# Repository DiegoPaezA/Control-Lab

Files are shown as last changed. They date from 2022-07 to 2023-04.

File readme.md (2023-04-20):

# Low-cost control laboratory kit - Control(LAB)

<p align="justify">Control(Lab) is developed following the <a href="https://is.gd/1HAwDJ">TCLab</a> idea: a printed circuit board (PCB) that allows connection with the Arduino processing unit. The board has three transistors that work as heaters and three temperature sensors to follow the temperature variations in each heater. The operation of the plant is based on the control of the electrical current that flows through the transistors using the pulse width modulation (PWM) generated from the system's processing unit. The control action generates a variation in the temperature of the plant heaters limited by software to 100°C. This variation is measured by the temperature sensors and registered in the Arduino, thus establishing a closed control loop.</p>

<p align="justify">To develop an affordable and easy-to-build control lab kit, low-cost and easily accessible elements were selected. The LM35 temperature sensor replaced the TMP36 temperature sensor used in the TCLAB reference plant; the new sensor fulfills the necessary operating and functionality ranges. The sensor is linear and generates a voltage output proportional to the temperature variation (T° C = 10mV). Also, it has calibrated precision of 1°C, its measurement range is -55 ° C to 150 ° C, and it has a guaranteed precision of 0.5°C at 25°C ambient temperature. Finally, the configuration of three TIP31C NPN transistors (BJTs) as heaters allows implementing controllers of the single-input-single-output (SISO) type or multiple-input multiple-output (MIMO) with a low-cost and accessible device. Figure 1 shows the Control kit (Lab).</p>

<p align="justify">This repository presents different examples focused on testing the operation of the different ESP32 functionalities using FreeRTOS. The examples have been validated using an ESP32 DEVKIT DOIT board and the documentation of each of the examples is being done to address the theoretical concepts of each of the topics addressed.</p>

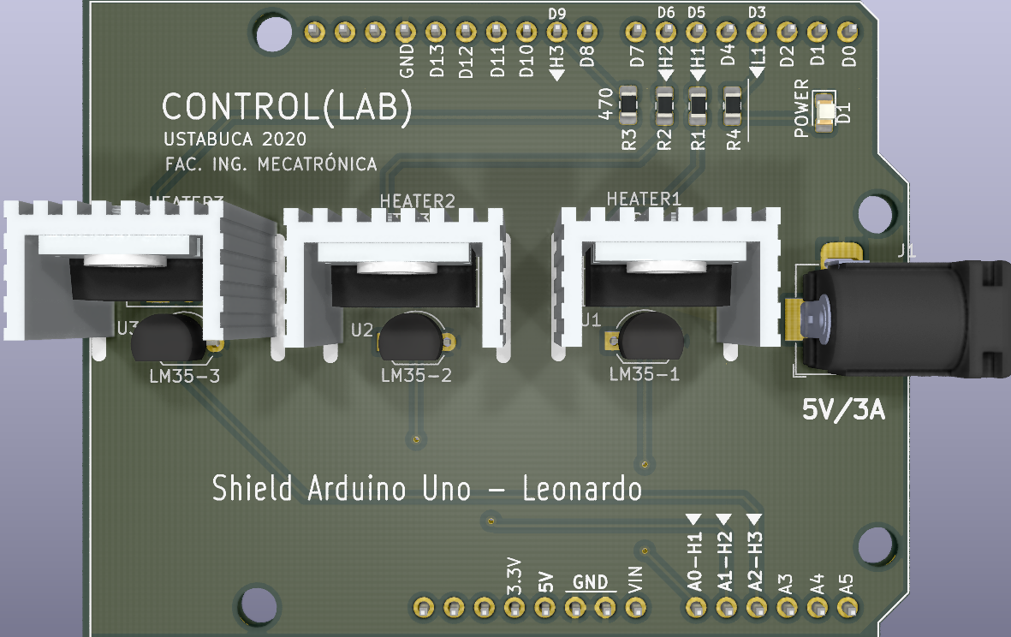
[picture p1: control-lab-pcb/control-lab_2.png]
Control Laboratory Kit - Control(Lab)


## References

Detailed description of the Control(Lab) can be find on the on the Article: [Comparative Study of PID, DMC, and Fuzzy PD+I Controllers in a Control Laboratory Kit](https://ieeexplore.ieee.org/document/9981589)

D. P. Ardila, D. M. Reyes, C. V. Niño, R. Tanscheit and M. Vellasco, "Comparative Study of PID, DMC, and Fuzzy PD+I Controllers in a Control Laboratory Kit," 2022 IEEE Latin American Conference on Computational Intelligence (LA-CCI), Montevideo, Uruguay, 2022, pp. 1-6, doi: 10.1109/LA-CCI54402.2022.9981589.

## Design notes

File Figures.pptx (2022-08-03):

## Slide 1

Fuzzy PD+I

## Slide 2

DMC

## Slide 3

PID

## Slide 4

Fuzzy PD+I + GA

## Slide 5

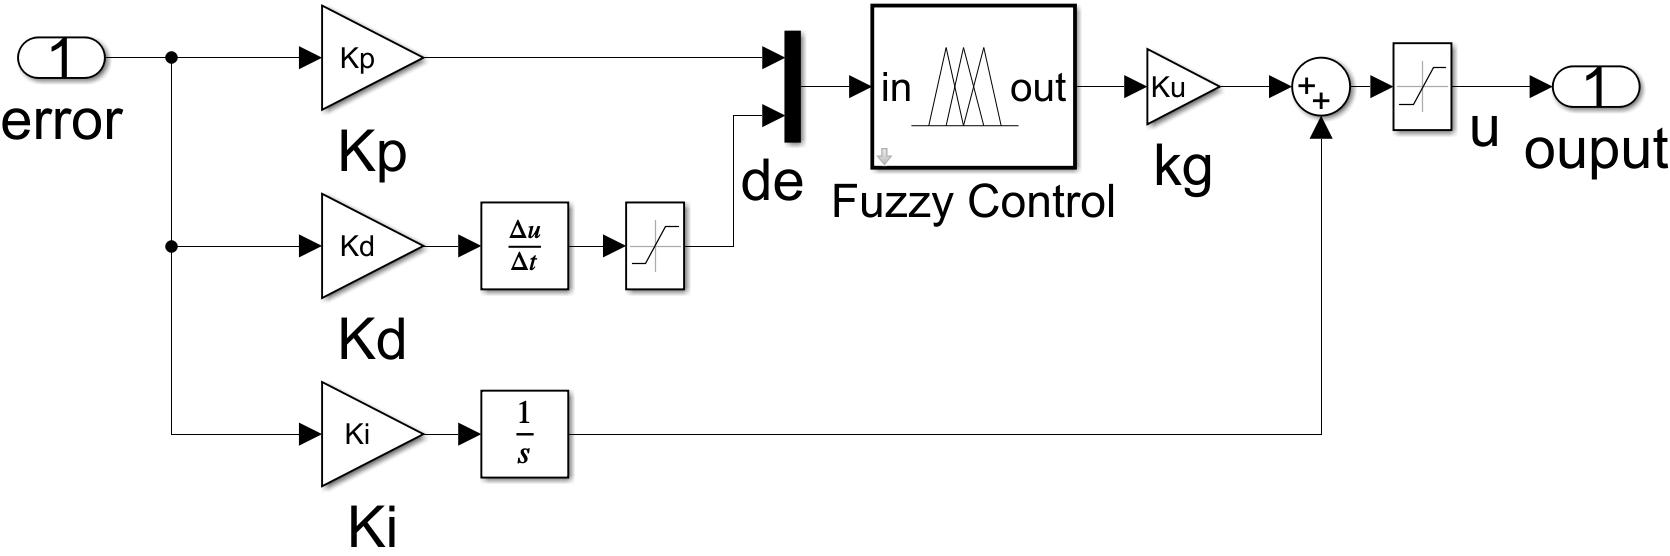
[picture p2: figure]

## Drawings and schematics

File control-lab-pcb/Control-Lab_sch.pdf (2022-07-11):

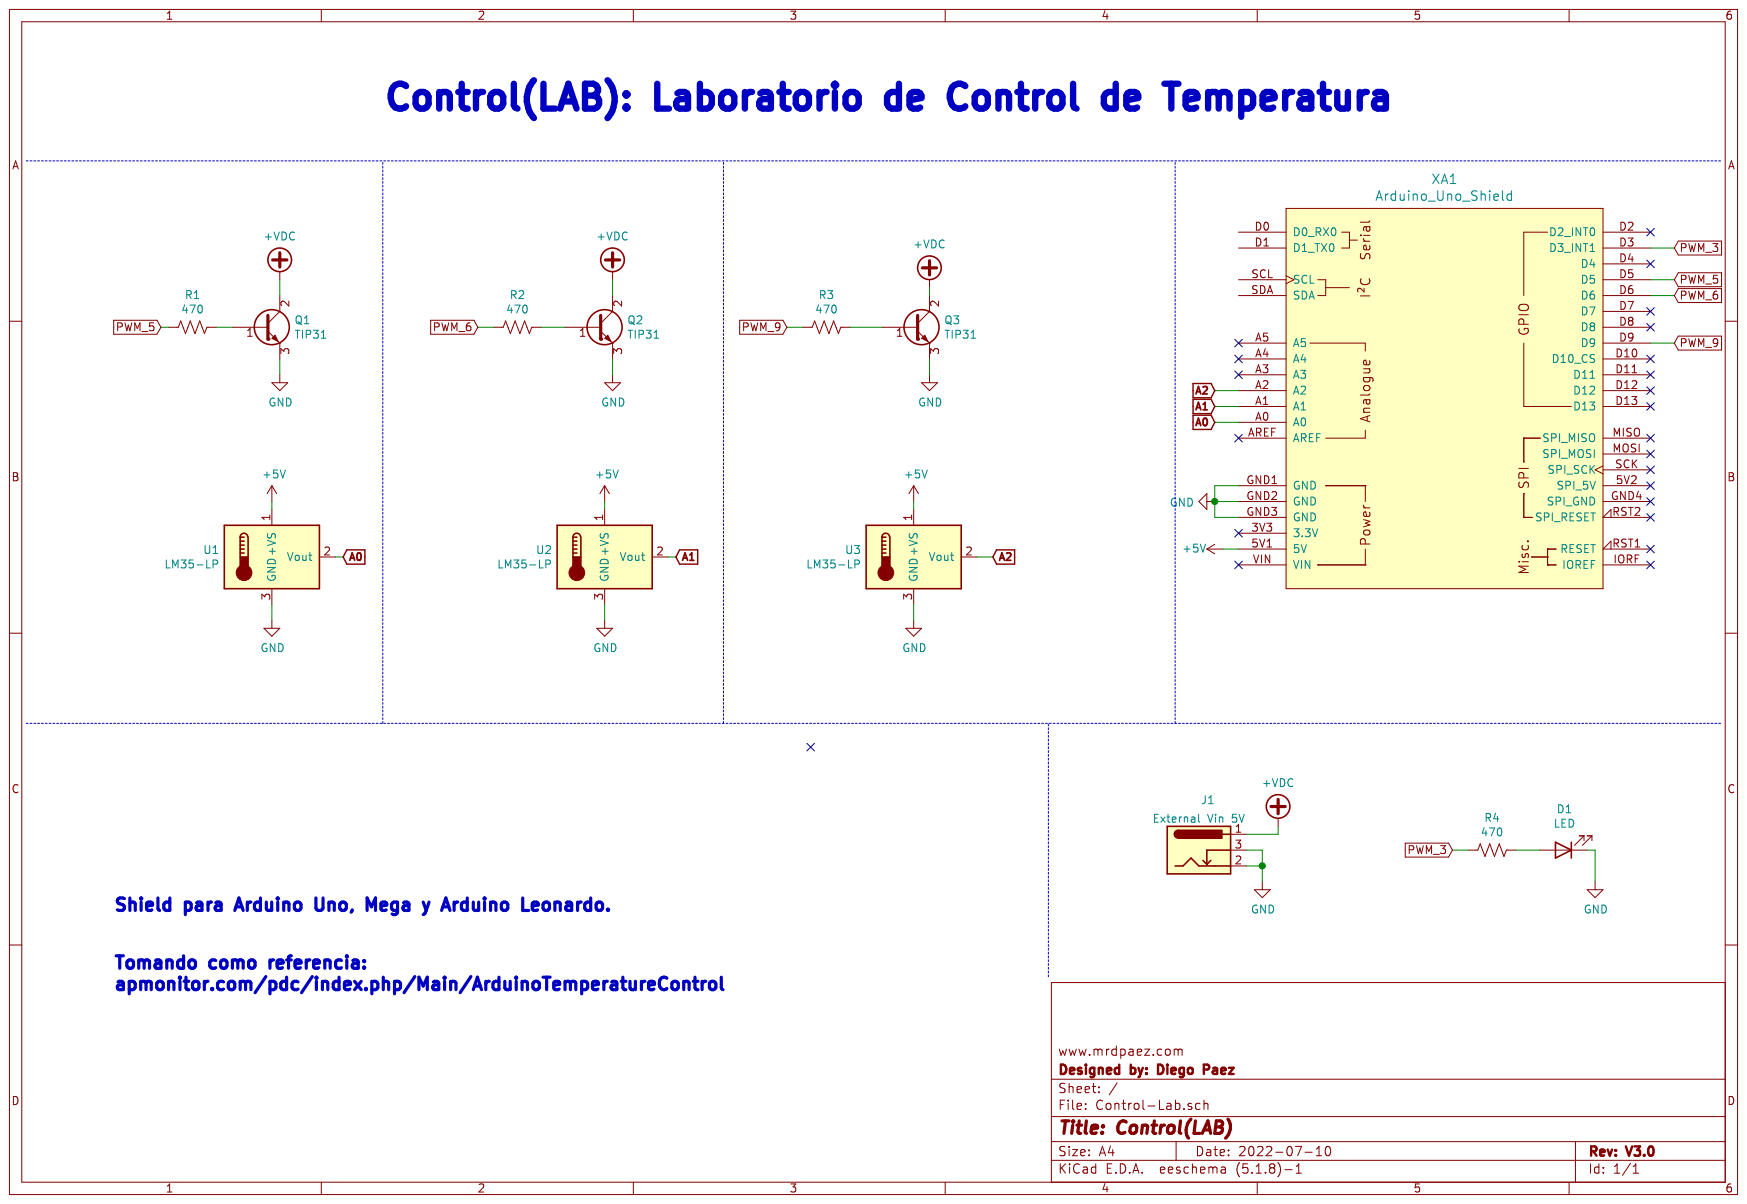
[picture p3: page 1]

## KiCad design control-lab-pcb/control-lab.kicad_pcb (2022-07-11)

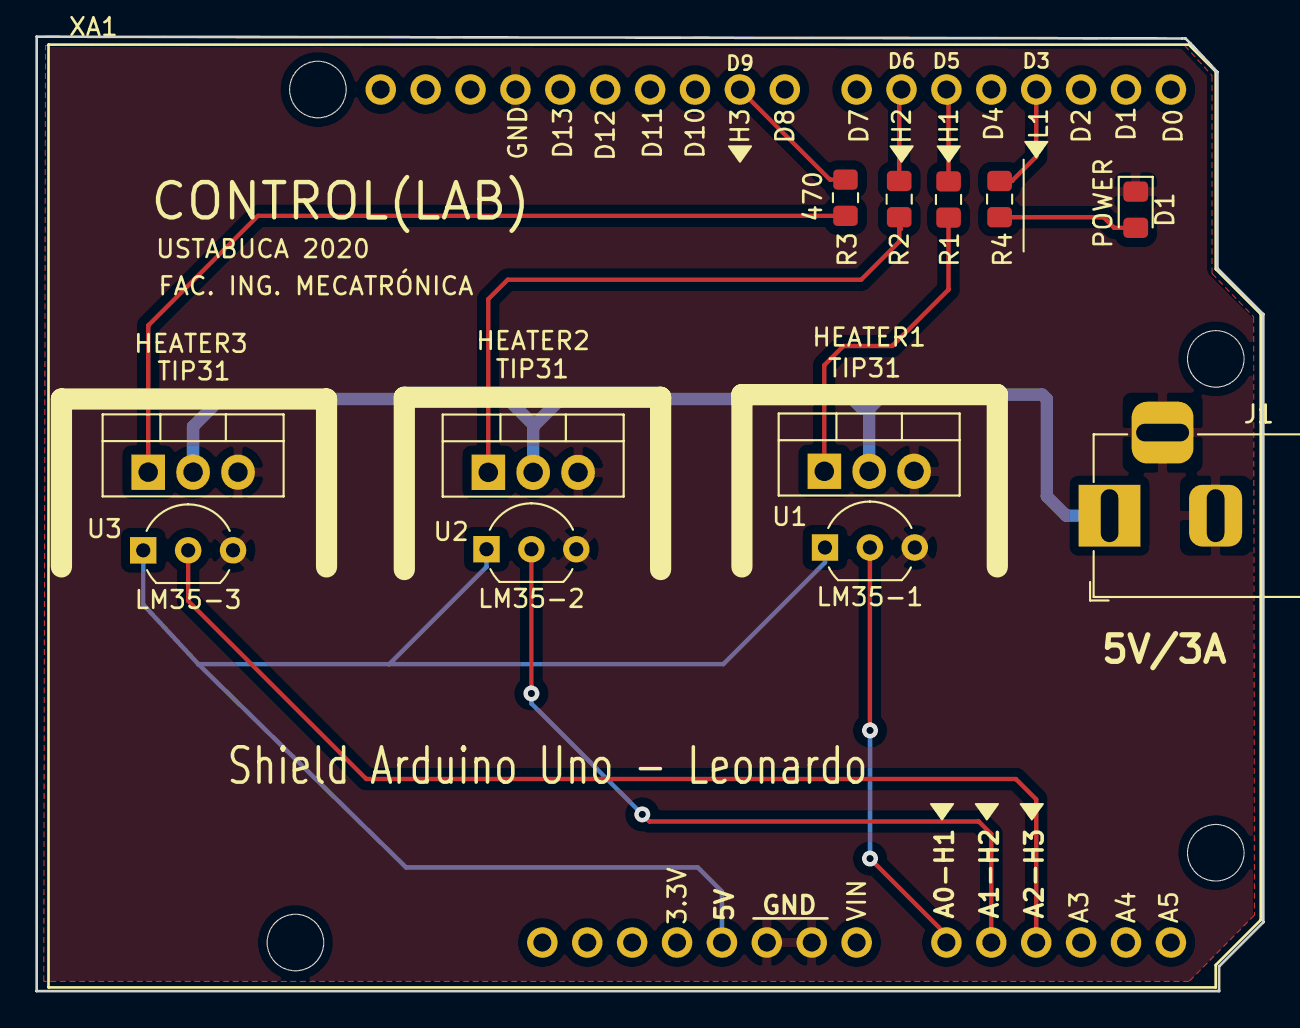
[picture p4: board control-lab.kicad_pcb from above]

Board: 2 copper layers, 69.4 x 54.0 mm, 13 parts (0 on the bottom side), 14 nets.

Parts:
D1: POWER; LED_0805_2012Metric_Pad1.15x1.40mm_HandSolder
HEATER1, HEATER2, HEATER3: TIP31; TO-220-3_Vertical
J1: External Vin 5V; BarrelJack_Horizontal
R1, R2, R3, R4: 470; R_0805_2012Metric_Pad1.15x1.40mm_HandSolder
U1: LM35-1; TO-92_Inline_Wide
U2: LM35-2; TO-92_Inline_Wide
U3: LM35-3; TO-92_Inline_Wide
XA1: Arduino_Uno_Shield; Arduino_Leonardo_Shield

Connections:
+5V: U1.1, U2.1, U3.1, XA1.5V1
+VDC: HEATER1.2, HEATER2.2, HEATER3.2, J1.1
A0: U1.2, XA1.A0
A1: U2.2, XA1.A1
A2: U3.2, XA1.A2
GND: D1.1, HEATER1.3, HEATER2.3, HEATER3.3, J1.2, J1.3, U1.3, U2.3, U3.3, XA1.GND1, XA1.GND2, XA1.GND3
unnamed: D1.2, R4.1
unnamed: HEATER1.1, R1.1
unnamed: HEATER2.1, R2.1
unnamed: HEATER3.1, R3.1
PWM_3: R4.2, XA1.D3
PWM_5: R1.2, XA1.D5
PWM_6: R2.2, XA1.D6
PWM_9: R3.2, XA1.D9

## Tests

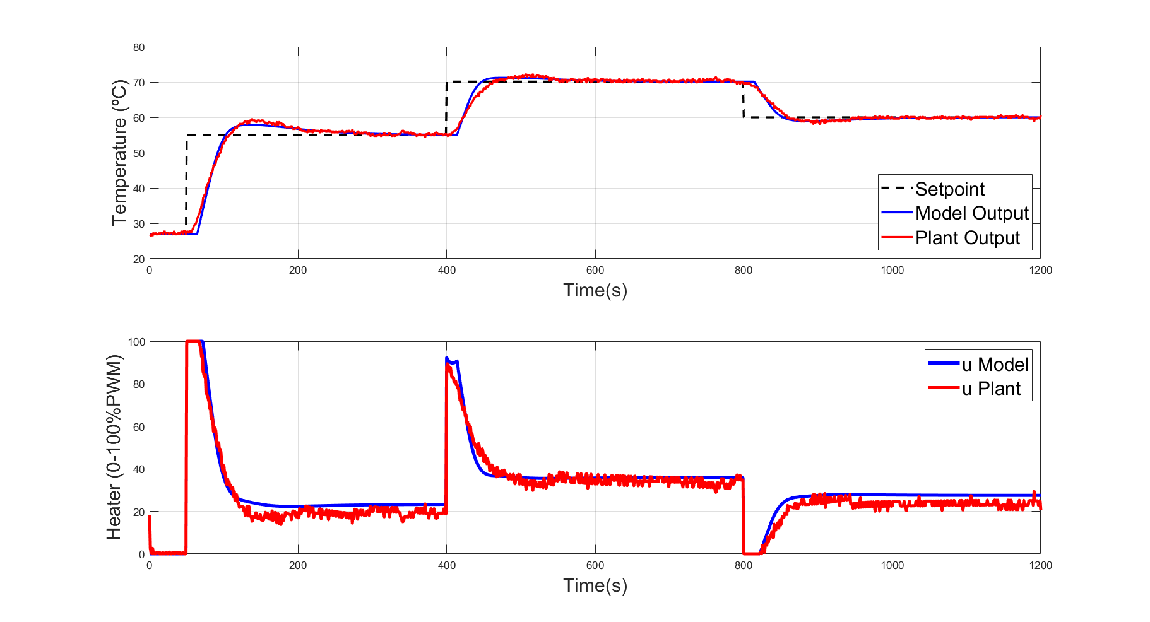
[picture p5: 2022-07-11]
Control_PID/resultado.png

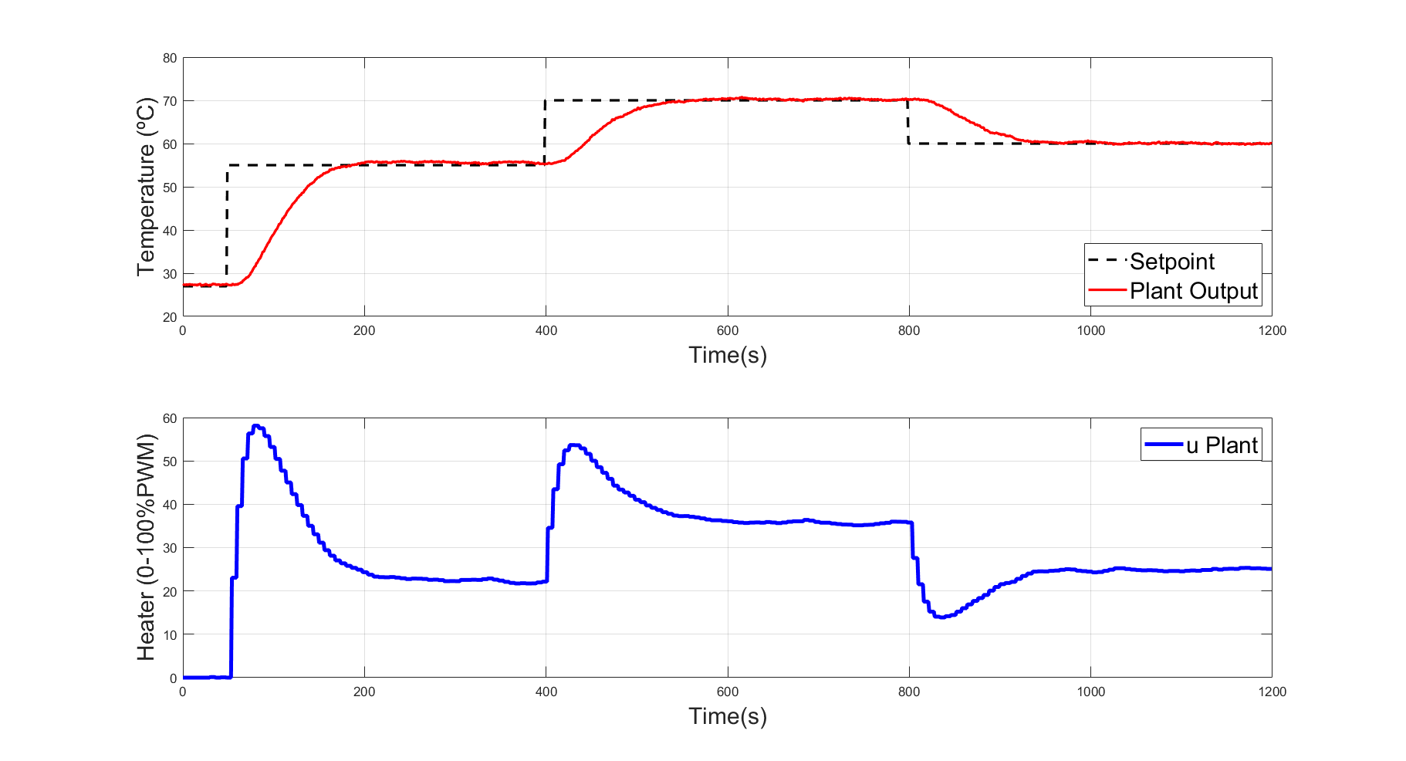
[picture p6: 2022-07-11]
Control DMC/resultados_planta.png

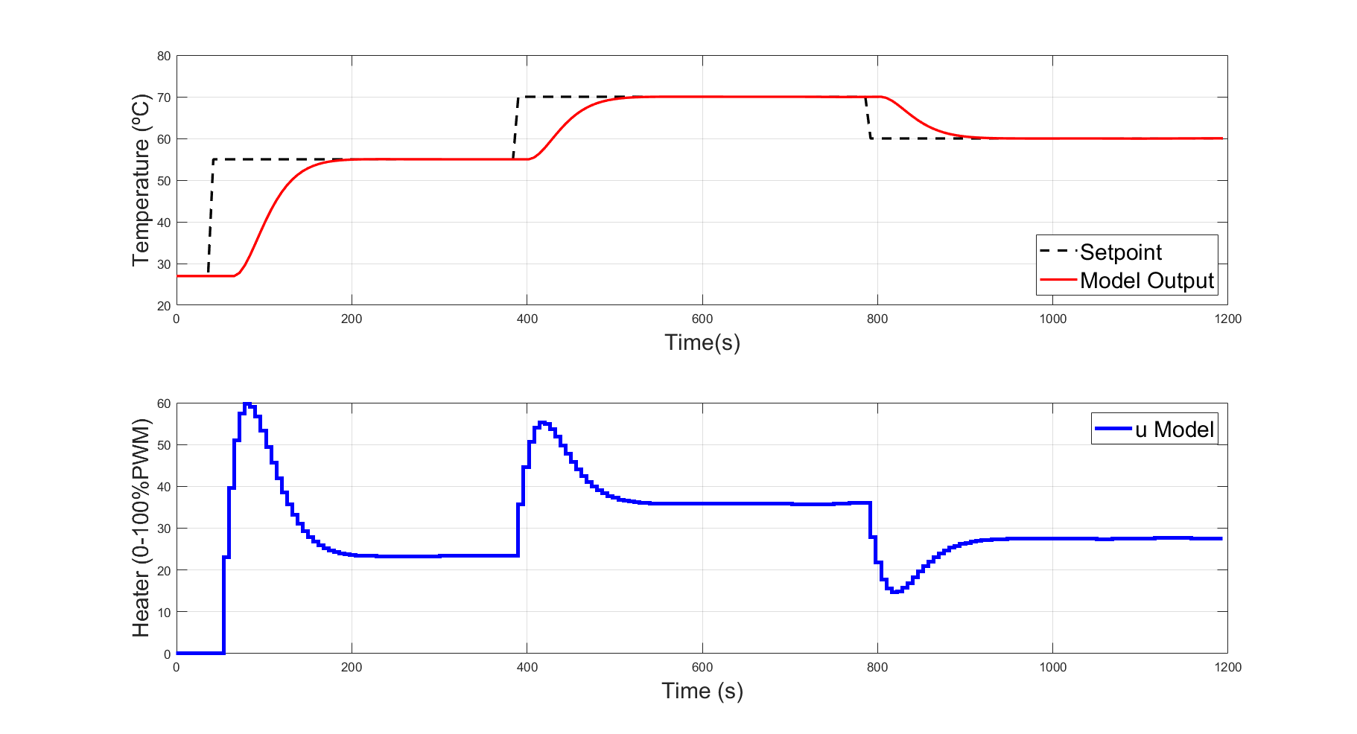
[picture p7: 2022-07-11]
Control DMC/resultados_modelo.png

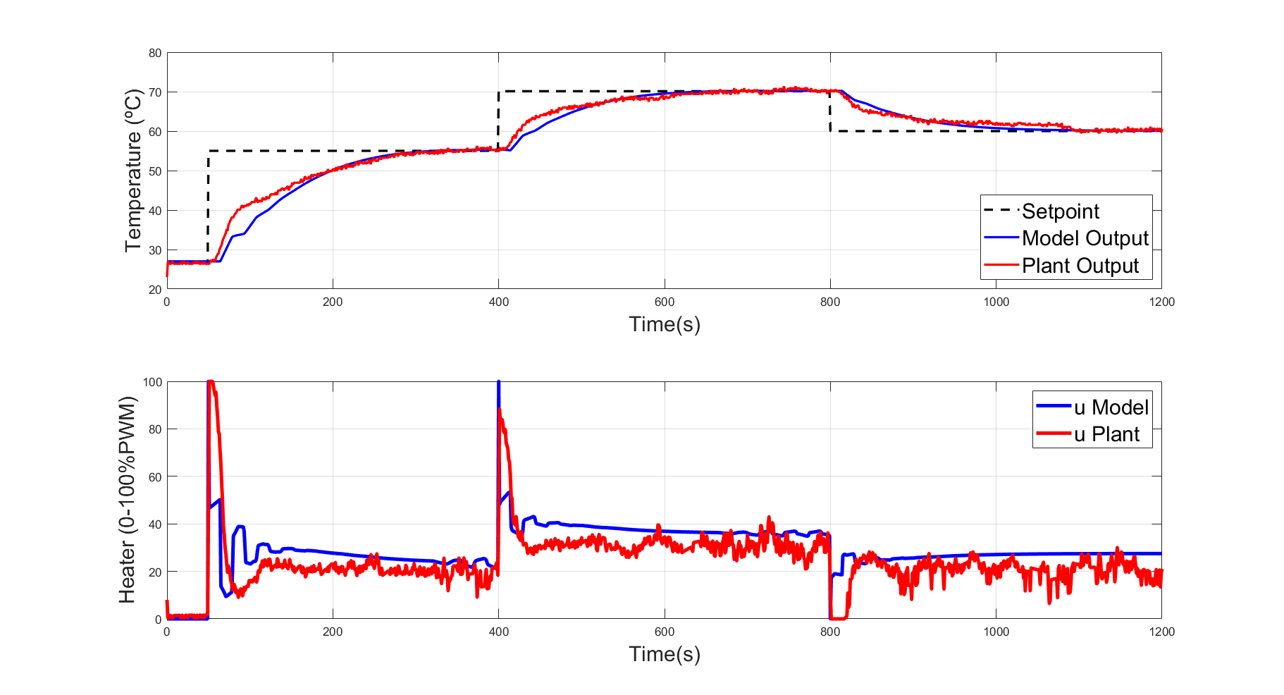
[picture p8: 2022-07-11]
Control PFuzzy/ResultadosFuzzyPID.png
